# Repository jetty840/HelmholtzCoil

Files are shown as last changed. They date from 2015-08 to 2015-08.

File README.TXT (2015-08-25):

Instructions
============

http://hackaday.io/project/7409-highly-configurable-3d-printed-helmholtz-coil

Summary
=======

Helmholtz coils contain a region of uniform magnetic field which is common used to measure the strength of magnets, measure electrical charges at the atomic level and nulling out earths magnetic field. The magnetic field calculation is done for you (no math).

This project uses OpenScad which is a 3D Solid modeler for 3D printing. OpenScad has the advantage that it's a programming language, which lends itself to heavy customization. You can custom everything, and if you don't like it or need something else, then change it.

Output in the OpenScad console details the coil configuration, wire length, field strength per Amp / mA and the maximum capacity of the coil:

Helmholtz Coil Configuration Statistics:
    AWG: 30
    Coil Diameter: 21cm
    Coil Turns: 3
        25649.22370 nT / 0.25649 Gauss per amp
        25.649224 nT per mA
        Wire length per coil: 1.98m
        Combined resistance of both coils: 0.001342Ohms
        Voltage required to drive coil: 0.00026979Volts @ 0.201Amps
        Maximum magnetic coil capacity: 5155.49396nT for
        the provded gauge
        Usable Volume (Cylinder): 105Length(mm) x 70Diameter(mm)

The inner cylinder of the coils (the space that is 1/3 the diameter of coil), denotes the area of uniform magnetic field.

The platform for magnetic experiments is replaceable, so you can have switchable platforms for applications.

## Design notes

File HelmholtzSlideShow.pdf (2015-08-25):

# Measuring Earths Magnetic Field

# using a

# Helmholtz Tangent Galvanometer

Tuesday, August 25, 15

# Items Required:

- Helmholtz Coil. Make one here: http://tinyurl.com/pes6tzp
- Benchtop Power Supply
- Connecting Wires
- Field Compass
- Multimeter (Amps Setting)

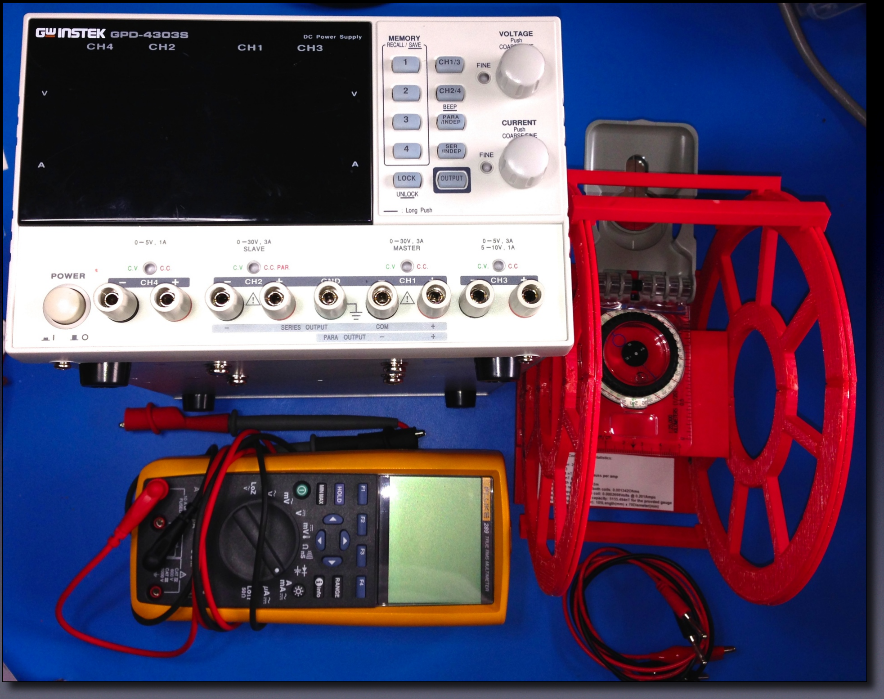
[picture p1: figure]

If you don’t have a benchtop PSU,

# you can substitute with a DC PSU

and Rheostat.

# IMPORTANT: Do not exceed the current rating of your Helmholtz coil and power supply

# Magnetic Components

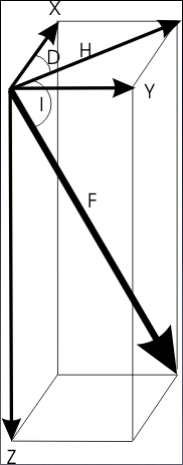
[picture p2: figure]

- There are a number of metrics for the Earths Magnetic Field. We’re interested in the Horizontal Magnetic Component, also known as “H” and is where a compass points when held on a level plane.
- More information on the various components: http://www.geomag.nrcan.gc.ca/mag_fld/comp-en.php

# Find A Magnetically Clean Location

- Use the compass to find a good location
- Move the compass around the location to detect sources of magnetism (ferrous metal objects, magnets, electronics etc.) and avoid them
- Find somewhere the compass points to Magnetic North for a few feet in all directions

# Connect Coil

- Connect the benchtop power supply via an Ammeter to the coil
- If using a regular power supply, connect via an Ammeter and a Rheostat, make sure that the Rheostat is set for minimum current

# Place Compass In Coils and Orientate North

- Ensure PSU is off
- Place the compass in the magnetically uniform cylinder inside the coil
- Orientate the coil so that Magnetic North is parallel with the plane of the wire in the coils
- This will mean that the cylinder through the coils will be lying East/ West

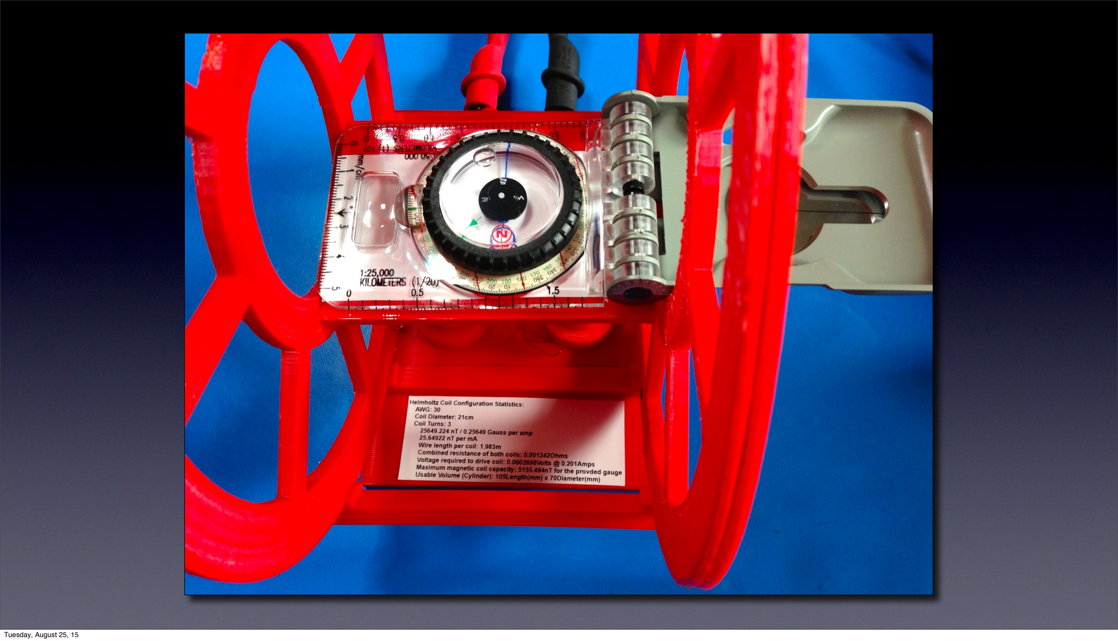
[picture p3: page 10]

# Some Theory - Tangent Law

Magnetic North (Bh)

Helmholtz Field (B)

Compass Needle

The Tangent Law Of Magnetism states, when you have a magnet in one direction and you apply a magnet at 90 deg, the resulting field is related by the tangent:

B = Bh x Tan(θ)

θ

# Some Theory - Tangent Law

Because Tan(45) = 1.0, if current is applied to the Helmholtz coil until the compass needle deflects from Magnetic North by 45 degrees, then B=Bh.

At this point the magnitude of the field in the Helmholtz coil is equal to the field of Magnetic North.

# Deflect Needle To 45 Degrees

- Increase current in the Helmholtz Coil until the needle deflects 45 degrees
- Note the current (Current 1)

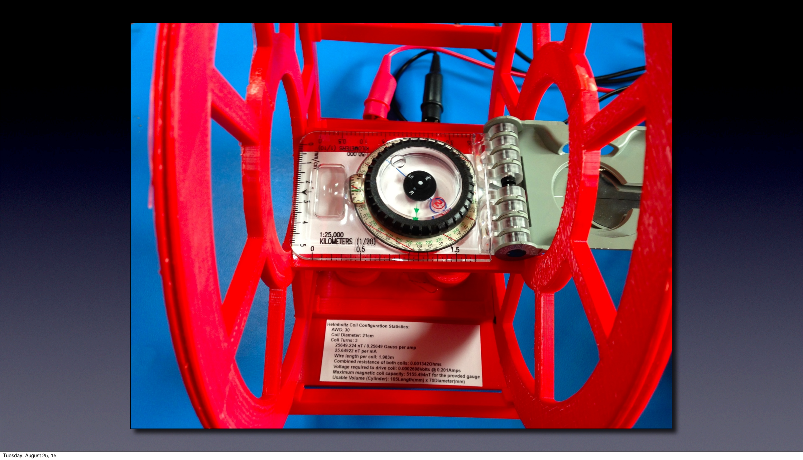
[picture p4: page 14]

# Deflect Needle To -45 Degrees

- Reverse the current in the coil so that the needle deflects in the opposite direction
- Increase current in the Helmholtz Coil until the needle deflects -45 degrees
- Note the current (Current 2)

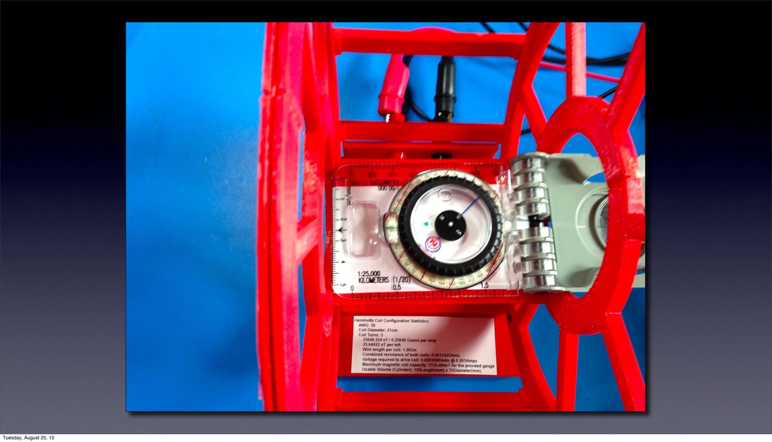
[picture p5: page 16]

# Average Current Readings

- We take 2 current measurements in the previous steps to reduce inaccuracy in our alignment
- Average the 2 current measurement, let’s call this I (current mA)

# Determine Coil Strength

- Figure out the nanoTeslas (nT) per mA for your coil. If you’re using my coil designer, then OpenScad provided that figure for you, otherwise:
- nT Per mA (S) = (899.17629 * N ) / R where:
- N = Number of turns on one coil
- R = Radius in millimeters

# Calculate Magnetic Earth Strength

- Using “S” (nT per mA) and “I” (average current of the Helmholtz Coil in mA), we have:
- Horizontal Magnetic Component in nT (Bh) = S * I

# Comparing Bh To Your Location

- Option 1: http://www.ngdc.noaa.gov/geomag-web/#igrfwmm (http://www.ngdc.noaa.gov/geomag-web/%23igrfwmm) Enter Latitude/Longitude and elevation. “Horizontal Intensity” is the Bh
- Option 2: http://geomag.nrcan.gc.ca/calc/mfcal-en.php Enter Latitude/Longitude. “H(nT)” is the Bh (http://geomag.nrcan.gc.ca/calc/mfcal-en.php)

# Music

Demain je change de vie - INSTRUMENTAL VERSION

Lohstana David

Jamendo

# License: Creative Commons CC-BY-SA

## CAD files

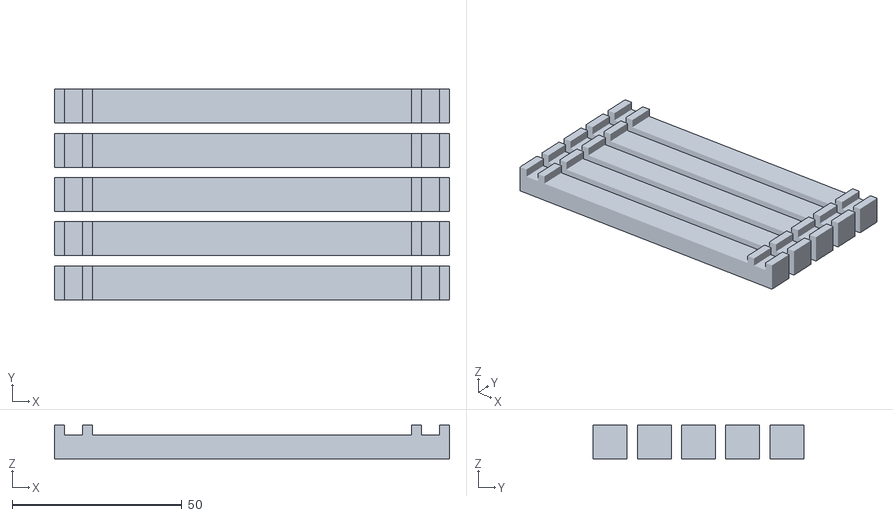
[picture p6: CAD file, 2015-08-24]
stl/CoilRetainers.stl
116.2 x 62.0 x 10.0

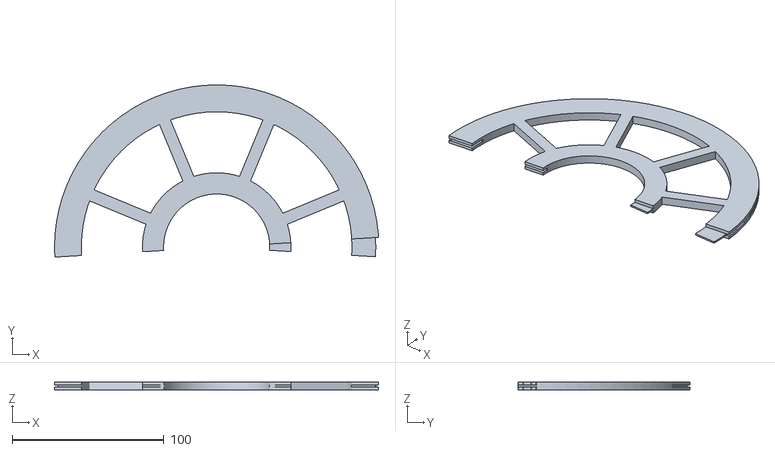
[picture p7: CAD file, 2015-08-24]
stl/CoilHalf2.stl
213.7 x 113.6 x 5.22

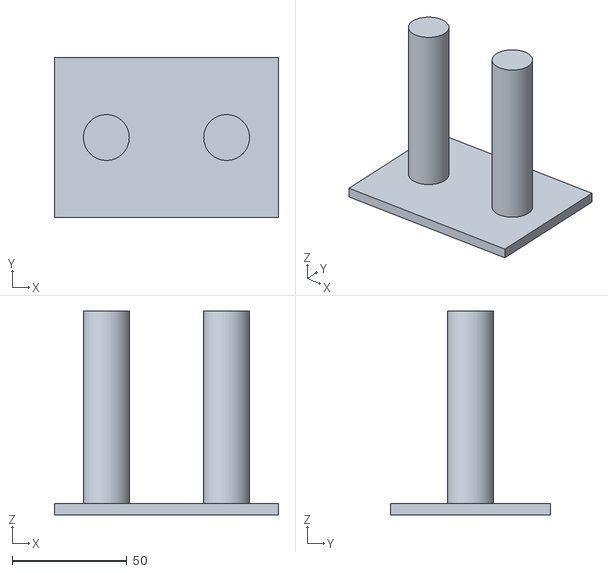
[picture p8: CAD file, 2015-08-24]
stl/Platform.stl
97.8 x 70.0 x 89.0

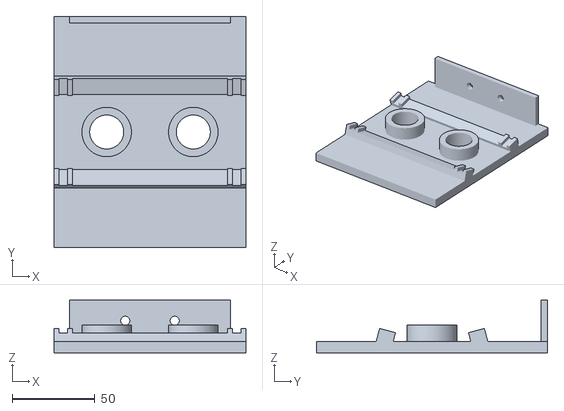
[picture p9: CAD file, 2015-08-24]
stl/MountingBlock.stl
116.2 x 140.0 x 32.0

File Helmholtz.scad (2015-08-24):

// Copyright: Jetty, 2015
// License: Creative Commons:  Attribution, Non-Commercial, Share-alike: CC BY-NC-SA
// https://creativecommons.org/licenses/by-nc-sa/2.0/

// Helmholtz Coil Design for 3D Printing.  Also this shows statistics about the coil generated, including the
// amount of field generated for a given number of wraps and current.

// Note: The coil diameter  + 2 * flange height must not exceed the width  of the 3D printer bed, and
// 		 The coil radius must not exceed the depth of the 3D printer bed.

// When winding the coils, both coils are wound in the same direction and mounted in the same direction, i.e. the current
// and magentic field in both coils is in the same axis.

// This will also do the calculation to figure out the magentic field strength
// Look in the output of openscad for "Helmholtz Coil Configuration Statistics" 
// Units are predominately nanoTesla (nT), as the earths field is generally measured in nT for magnetometers, if you need Gauss:
// 		1 Guass = 100,000nanoTesla

// Earths field is approximate +/-50,000nT, therefore the coil needs to be capable of at least that if cancelling the earths fields is required
// Kp Index 9 (highest for Aurora) is 500nT difference

// Printing:
//		If the diameter of the coil fits on the printer bed, then print 3 (CompleteCoil), otherwise if the radius of the coil
//		fits on the printed bed, then print 1 and 2 (the coil halves)
//
//		Coil halves - 10% infill, 2 shells and full support (including exterior)
//		Platform - 5% infill, 2 shells
//		Everything else, 10% infill, 2 shells
//
// Assembly:
//		Note the bottom of each coil has a small hole for the wire to go through, when assembling coil halves, make sure you have that
//		hole in each assembled coil.

partnum							= 0;			// 0=All, 1=Coil Half 1, 2=Coil Half 2, 3=CompleteCoil, 4=Coil Retainers, 5=Mounting Block, 6=Platform


// All the following settings are metric except coilOhmsPerThousandFeet and control the magnetic strength, size of
// the coil and statistics for the coil, they need to be set correctly
coilRadius						= 105;		// Coil Radius in mm's
coilGauge						= 30;		// Just for reference, not used in any calculations
coilNumberOfTurns				= 3;			// The number of turns in each coil
coilWireDiameter					= 0.34;		// Wire diameter in mm's, note this includes insulation (insulation thickness varies)
coilWireFudge					= 0.2;		// Fudge factor in mm's to add to the space for the coil to allow for 3D printer inaccuracy	
coilFormerFlangeHeight			= 2.0;		// The height of the flange, must be at 3X the coilWireDiameter + coilWireFudge to allow for the wire hole
coilFormerFlangeWidth			= 2.0;		// The width of the flange
coilMaxAmps						= 0.2010;	// Base this on the maximum current the coil can safely take and that can
											// be delivered by the PSU for the guage of wiring you're using.
											// Reference: http://amasci.com/tesla/wire1.html   (Amps or MaxAmps column)
coilOhmsPerThousandFeet			= 103.19;	// Ohms per thousand feet of wire:
											// Reference: http://amasci.com/tesla/wire1.html (Ohms/Kft)

// These settings effect general coil geometry
coilOuterRingPercentage			= 1 - 0.15;	// The size of the outer ring based on a percentage of the radius
coilInnerRingPercentage			= 0.20;		// The size of the inner ring based on a percentage of the radius

// These settings effect parts of the total object
coilRetainerThickness			= 3;
coilRetainerWidth				= 10;
coilRetainerDepth				= 7;
coilNumRetainers					= 5;			// The number of retainers when partnum=4 (always 2 less than the actual number, as 2 are part of the base
coilMountingBlockThickness		= 7;
coilMountingBlockWidth			= 140;		// It would make sense to make this wide enough to place the mounting posts outside of the coil for
											// magnetic field uniformity reasons
mountingPostBlockHeight			= 25;
mountingPostBlockThickness		= 4;
mountingPostDiameter				= 5.5;
platformHeightAdd				= 10;			// The height of the table can be increased by a positive number here
platformThickness				= 5;
platformPostDiameter				= 20;
platformPostReinforcementFudge	= 0.3;			// Post reinforcement diameter fudge factor for fit
platformPostReinforcementDiameter	= platformPostDiameter + 5 * 2; 
platformPostReinforcementHeight	= 10;



// DO NOT CHANGE THESE SETTINGS !
coilFormerWireSpaceThickness		= coilWireDiameter * coilNumberOfTurns + coilWireFudge;	// The space for the wire to fit in on the former
coilOhmsPerMeter					= (coilOhmsPerThousandFeet / 1000.0) / 0.3048;

manifoldCorrection 				= 0.1;


// These are used to figure out the magnetic force for the coil
// Reference: https://en.wikipedia.org/wiki/Helmholtz_coil
// DO NOT CHANGE THESE SETTINGS !
coilStatsUo						= 4 * PI * 1E-7;		// Uo term
coilStatsI						= 1.0;						// Coil current in amps (leave as 1)
coilStatsN						= coilNumberOfTurns;
coilStatsR						= (coilRadius + coilWireDiameter / 2) / 1000;
coilStatsB						= pow( 4/5, 3/2 ) * ((coilStatsUo * coilStatsN * coilStatsI ) / coilStatsR);	// Result is in Teslas	
coilStatsLengthPerCoil			= 2 * PI * coilStatsR * coilStatsN;
coilCombinedResistance			= (coilStatsLengthPerCoil / 1000) * 2 * coilOhmsPerMeter;
coilVoltageRequired				= coilMaxAmps * coilCombinedResistance;
coilMaximumCapacity				= (coilStatsB * 1000000000) * coilMaxAmps;
coilUsableDiameter				= coilRadius * 2/3;
coilUsableLength					= coilRadius; 
coilFormerTotalThickness			= coilFormerWireSpaceThickness + coilFormerFlangeWidth * 2;
coilSpokeRotationAngles			= [22.5, 67.5, 112.5, 157.5, 202.5, 247.5, 292.5, 337.5];
coilSpokeLength					= coilRadius - (coilUsableDiameter / 2) - 2.0;
coilSpokeDimensions				= [0.075 * coilRadius, coilSpokeLength, coilFormerTotalThickness];
coilSpokeOffset					= [0, (coilUsableDiameter + coilSpokeLength) / 2 + 1.0, 0];
coilFormerFlangeOffset			= [0, 0, (coilFormerWireSpaceThickness + coilFormerFlangeWidth) / 2];
coilHalferFlangeDimensions		= [(coilRadius + coilFormerFlangeHeight) * 2,
								   coilRadius + coilFormerFlangeHeight,
								   coilFormerFlangeWidth + manifoldCorrection * 2];
coilHalferWireSpaceDimensions		= [coilRadius * 2, coilRadius, coilFormerWireSpaceThickness + manifoldCorrection * 2];
coilHalferWireSpaceOffset			= [0, coilRadius / 2, 0];
coilHalferFlangeOffset1			= [0, (coilRadius + coilFormerFlangeHeight) / 2 + manifoldCorrection,   coilFormerFlangeOffset[2]];
coilHalferFlangeOffset2			= [coilHalferFlangeOffset1[0], coilHalferFlangeOffset1[1], - coilFormerFlangeOffset[2]];
coilHalferRotataionFlangeAngle	= 7;
coilOffset1						= [0, 			  0,   			   coilRadius / 2];
coilOffset2						= [coilOffset1[0], coilOffset1[1], - coilOffset1[2]];
coilRetainerDimensions			= [coilUsableLength + coilFormerTotalThickness + coilRetainerThickness * 2, coilRetainerWidth, coilRetainerDepth];
coilRetainerBlockDimensions		= [coilRetainerThickness, coilRetainerWidth, coilRetainerThickness];
coilRetainerBlockOffset1			= [(coilFormerTotalThickness + coilRetainerThickness) / 2,
								   0,
								  (coilRetainerDimensions[2] + coilRetainerBlockDimensions[2]) / 2]; 
coilRetainerBlockOffset2			= [- coilRetainerBlockOffset1[0], coilRetainerBlockOffset1[1], coilRetainerBlockOffset1[2]];
coilRetainerLocationAngles		= [-45, 45, 75, 105, 135];
coilRetainerLocationAnglesBlock	= [-15, 15];
coilMountingBlockDimensions		= [coilRetainerDimensions[0], coilMountingBlockWidth, coilMountingBlockThickness];
coilMountingBlockOffset			= [0, 0, - (coilRadius + coilFormerFlangeHeight + coilMountingBlockDimensions[2] / 2) ];
mountingPostBlockWidth			= (coilRadius - (coilFormerWireSpaceThickness + coilFormerFlangeWidth)) - 4;
mountingPostBlockDimensions		= [mountingPostBlockWidth, mountingPostBlockThickness, mountingPostBlockHeight];
mountingPostBlockOffset			= [0, ( coilMountingBlockDimensions[1] - mountingPostBlockDimensions[1] ) / 2,
								   ( mountingPostBlockDimensions[2] + coilMountingBlockDimensions[2] ) / 2];
mountingPostOffset1				= [15, 0, 0]; 
mountingPostOffset2				= [-mountingPostOffset1[0], mountingPostOffset1[1], mountingPostOffset1[2]];
platformDimensions				= [mountingPostBlockWidth, coilUsableDiameter, platformThickness ];
platformOffset					= [0, 0, -(platformThickness / 2 + coilUsableDiameter / 2) + platformHeightAdd];
platformPostOffset				= [coilRadius * 0.25, 0, 0];


$fn = 80;


helmholtzStats();



if ( partnum == 0 )
	coilRetainersAll();

if ( partnum == 1 )
	bottomHalfHelmholtzCoil();

if ( partnum == 2 )
	topHalfHelmholtzCoil();

if ( partnum == 3 || partnum == 0 )
	fullHelmholtzCoil();

if ( partnum == 4 )
	coilRetainersAllFlat();

if ( partnum == 5 || partnum == 0 )
	coilMountingBlock();

if ( partnum == 6 || partnum == 0 )
	platform();



module platform()
{
	postHeight				= platformOffset[2] - coilMountingBlockOffset[2] + (coilMountingBlockDimensions[2] + platformThickness) / 2;
	postHeightOffset 		= coilMountingBlockOffset[2] + (postHeight - coilMountingBlockDimensions[2]) / 2;
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

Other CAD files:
stl/CoilHalf1.stl
